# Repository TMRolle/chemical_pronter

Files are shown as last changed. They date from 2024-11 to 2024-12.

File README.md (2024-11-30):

# chemical_pronter

This repo contains CAD files (and soon assembly instructions) for a modular fluid routing system designed for chemical printers. It is readily and inexpensively manufacturable at home with a 3D printer and inexpensive off the shelf materials.

## The design premise

In ye olden days of yore, chemists didn't have any of that fancy ground glass stuff that's so popular in chemistry labs today. They had stoppers and tubes, and by golly it worked. When you needed to connect a flask up to a distillation column, you shoved a stopper with a hole in it into the top of the flask, put in a little stubby bit of flint glass tubing while trying not to stab yourself, and then stuck some silicone tubing (or latex, if you were a poor) on to that. You then shoved the other side of the squishy tube onto your condenser, which had hose barb fittings because back in cave man times that's all we had.

If you needed a reflux column instead, you connected the tube to the other end of the condenser, and bob's your uncle.

You could actually assemble a lot of fun and handy apparatus with nothing but basic flasks and rubber tubing. It may not have been as elegant as 24/40 ground glass fittings, but the only part you really needed ground glass on was your sep funnel, which is why sep funnels cost roughly a bajillion dollars back then. Anyway, the point is, it worked, and was doable with garage equipment.

This system is very loosely inspired by that approach. But instead of plugging up tubing and stoppers with our primitive sausage-fingers, this system does it all with valves. One specific type of valve in particular. But we'll get to that in a second.

## The abstraction

Most "things" that you will encounter in a chemistry lab can be accurately represented with the following ludicrously oversimplified model:

fluid input--->[device]---->fluid output

For example, let's take the condenser. If we ignore the water circulating through the jacket, a fluid (in the proper sense - liquid or gas) goes in one end and out the other.

If you want to reflux something, you would attach the bottom of the condenser to a boiling flask, and leave the top open. The flow would thus be something like this:

Boiling flask ---> condenser bottom ---> condenser top ---> open air

But what if you want distillation? Well, we need a second flask, but that's about it. That flow would look something like:

Boiling flask ---> condenser top ---> condenser bottom ---> receiving flask ---> [open air, or vacuum if you're fancy like that]

So all we need to move between these two setups is to change which end of the condenser goes to the boiling flask, really, and if we're feeling ambitious to skip the recieving flask.

This abstraction generalizes well. Most lab apparatus can be assembled with each "device" being considered as some arbitrary thing with a fluid input and a fluid output, and tubes in the right places to hook all the right inputs to all the right outputs.

So, that's what the valve does.

## The valve

If you're a valve nerd, this is technically a 3-position 4-way valve. On the "input" side, you have three ports: device port A, device port B, and main loop in. These ports are just holes drilled in a round disk around a central axis, like a triforce or something, but with round holes instead of triangles. This is because drill bits for drilling triangular holes are really expensive.

So tubes go into one side of this plate, and on the other side of the plate is another round plate, also with three holes. The second plate rotates, allowing the three holes on the stationary plate to line up with the three holes on the mobile plate in any one of 3 positions. 

On the mobile plate, there is one port - main loop out - and the other two holes are just connected with a short piece of tubing.

What this allows you to do is put a device in any one of three positions:

### Bypass

If main loop in is lined up with main loop out, then the device is skipped entirely. The device's port A and port B are attached to each other, if you care about that sort of thing, which you probably don't.

### Forward

If the mobile plate is rotated 120 degrees clockwise, things start to get interesting. Now, the path is:

main loop in ---> short loopback tube ---> device port A ---> [device] ---> device port B ---> main loop out

We've effectively diverted the flow, and added our device to the main path!

### Reverse

If the mobile plate is rotated 120 degrees *counterclockwise*, then things get even more interesting. Now the path is:

main loop in ---> device port B ---> [device] ---> device port A ---> short loopback tube ---> main loop out

Simply by changing the valve position, we have "flipped our condenser upside down" so to speak. If our device is a condenser, that is. But anyway, we're still diverting the main flow through our device, but now it's going through our device in the other direction.

## The implication

This means that you can take all your equipment - your pumps, your reactor, your condensers, a bunch of old mason jars filled with solvents and reagents, your filtration setup, whatever - throw it all in one big main loop, and then let the software figure out how to hook it all together to make whatver setup you need. It effectively reduces apparatus assembly into a software pathfinding challenge, and any software guy can tell you, if there's a way, A* will find it.

But most importantly, you can serialize operations. With just software. A 10-step synthesis can be performed by literally just putting the right starting materials in the right jars, hitting "print", and walking away.

Actually no, please don't walk away, it probably is a good idea to keep an eye on it with a fire extinguisher, just in case. But you get the idea.

Also, side note, a loop can be a device too, allowing for subloops. This probably has some implications or something, if I knew topology better maybe I could tell you what they were. 

# The Files

There is one main CAD file, in FreeCAD format. This contains 4 PartDesign bodies, 3 for the printable parts and one containing a 2D sketch for the PTFE plate, which can be laser cut on a typical CO2 laser (60W or above recommended). 3D printed parts should be printed in PLA+ (we like eSun brand) with a standard 0.4mm nozze and 0.2 layer height on "strong" defualt settings, unless otherwise indicated.

## valve_plate

The 2D drawing for the valve plate, to be cut out of PTFE plate material. You need to cut two of these per valve. The design is for 1/4in plate, but you can probably get away with 6mm as the minimum sheet thickness. Thicker is fine, thinner is not recommended. Export as DXF and then cut on your laser cutter. A jig may be added later if there is demand for it.

## valve_base

This should be printed with the fancy-lookin bit flat on the bed. It holds the stationary plate, the axle for the mobile plate, and the BYJ48 stepper motor.

## stationary_housing and mobile_housing

These should be printed, in "cup" orientation, with the flat part flat against the bed. These will serve both as the holders for the PTFE plates and as lapping fixtures during assembly.

# Assembly

**(todo: pictures and more details)** 

The two laser cut plates should be affixed into each of the "housing" parts, with the big holes aligned. The little holes can accomodate M2 screws to hold the plate in postion, no tapping is needed for this.

Once the plates are in their holders, take a flat piece of granite (or glass, in a pinch) and stick a wet piece of ~200 grit sandpaper to it, rough side up. Add some water on top, it should be really wet. You will now place the exposed face of the PTFE plate against the wet sandpaper surface, *gently* push down to keep it flat against the wet sandpaper/granite plate, and gently move in a figure 8 motion. You don't need to remove much material here, this is just to ensure both plates are flat. You should repeat this process again with finer sandpaper, I recommend a pass with 200, 600, and 1200 grit. Do this for both parts. If you've done it right, then when the plates are wet, they should stick together a little just by suction.

Next, tap the big holes with an M8 tap. You will be fabricating fittings to go into each of these holes. A future design may use off the shelf fittings and/or 1/8in NPT fittings.

## ToDo: Finish the rest of the docs

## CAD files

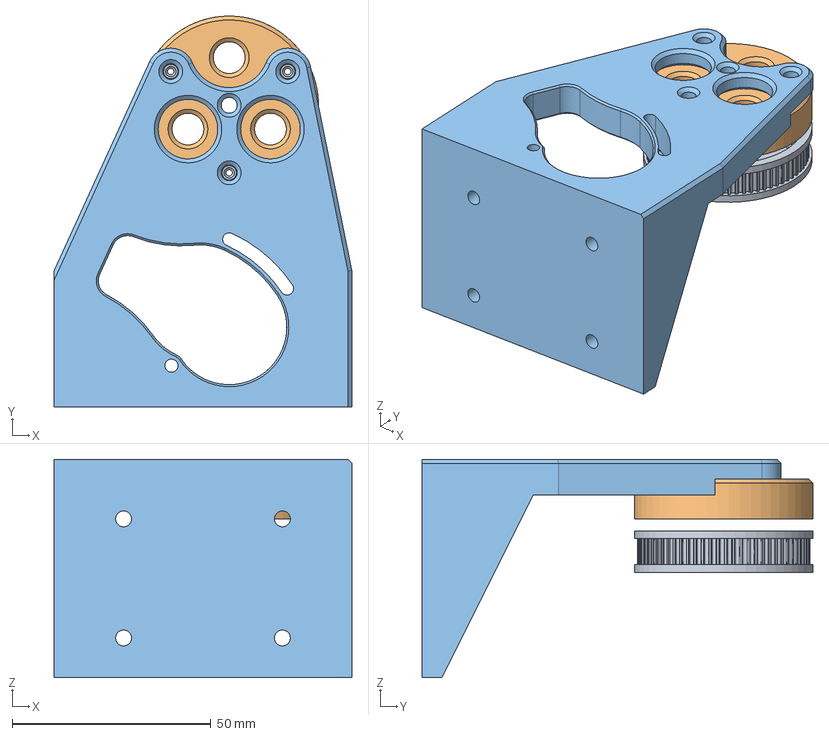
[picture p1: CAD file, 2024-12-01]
CAD/Valve.fcstd
75.0 x 98.5 x 55.0 mm
mobile_housing
stationary_housing
valve_base

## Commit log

2024-11-30 Update README.md
    Adding more descriptions and assembly info
2024-12-01 minor naming updates
    [Valve.fcstd]
